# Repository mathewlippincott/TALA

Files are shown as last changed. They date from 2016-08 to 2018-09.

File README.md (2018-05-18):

### Introduction to the TALA
The TALA, or Tethered Aerodynamic Lifting Anemometer, is a type of [Kite Wind Speed Meter](https://github.com/mathewlippincott/Kite-Wind-Speed-Meter) or anemometer, a device for measuring the wind speed at the kite using ground-based measurements. 
The TALA repository consists of the [TALA kite](TALA_Kite), kite-specific [corrections to ground-based measurements](TALA_Measurement), as well as a kit of recommended tools for taking the required ground based measurements. Together these components form the TALA kit.
 
### Current TALA kit 
* The [TALA kite](TALA_Kite)
* [Lookup tables and equations](TALA_Measurement) for extrapolating air speed from measurments by:
 * correcting altitude measurements for line sag
 * correcting wind speed measurements for air density
* A [Measurement procedure](TALA_Measurement)
* Measurement equipment:
 * Spring scale for line tension
 * marked kite line for counting the amount of line in the air (or fishing line length counter) 
 * compass for wind direction
 * inclinometer for the angle of the kite 
 * thermometer for ground temperature
 * barometer for ground pressure

### Designers of the TALA
The kite was originally designed by Raymond P. Holland Jr. and adapted by Charles F. Woodhouse for anemometry into the TALA product sold by Approach Fish until some time in the early 1990's. The invention is covered by expired US patents 3,767,145, 4,058,010, 4,152,933 & 4,221,351.
	These plans are released under the [CERN OHL 1.2](LICENSE.MD), compiling [ongoing Public Lab research](www.publiclab.org/wiki/kite-anemometers) on the TALA into a DIY kit.
	
The TALA was imagined as an automated kite flight and measurement system providing local weather conditions at airports, but was usually flown by hand with a spring gauge used in the current TALA kit. Learn more about the [TALA and kite anemometer research in the Public Lab Wiki.](https://publiclab.org/wiki/kite-anemometers)

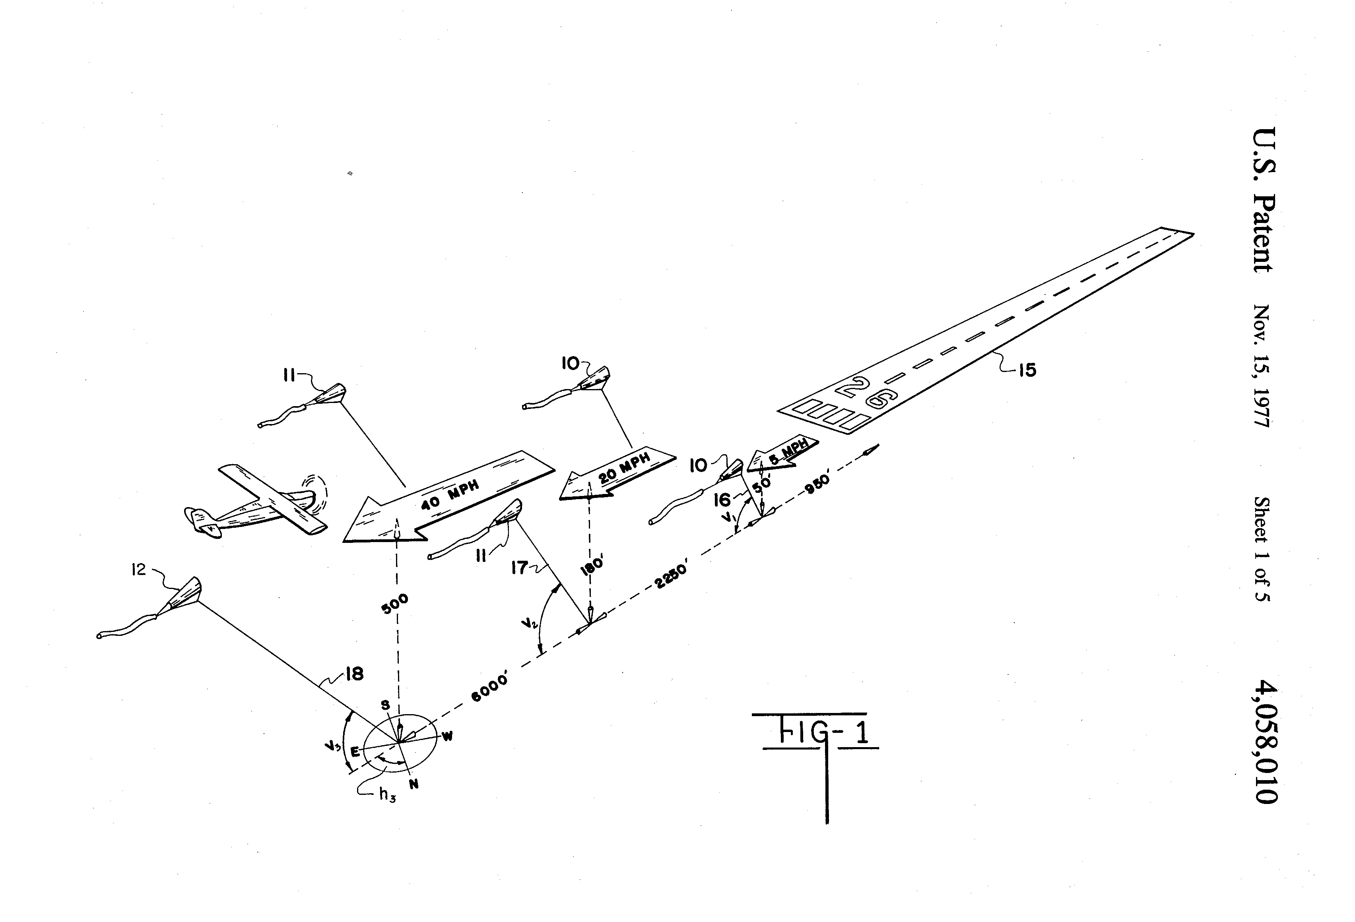
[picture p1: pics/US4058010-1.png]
TALAs at an airport


### About this project
The TALA repository is a project of [Mathew Lippincott](headfullofair.com) and [@Ecta64](http://publiclab.org/profile/ecta64) to create a stable device replicating the TALA and licensed under [CERN OHL 1.2](LiCENSE.md).

To read more about using kite anemometers and find resources and sources used in this repository, visit [headfullofair.com/tags/kite-anemometers](headfullofair.com/tags/kite-anemometers). 

### [contributing](contributing.md)
To learn more about contibuting, please read our [contribution guidelines](contributing.md).

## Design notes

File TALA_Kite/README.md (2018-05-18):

### The TALA Kite
The TALA kite is a type of sled kite. It is 1500cm^2 of surface area and the main sheet weighs 16g.  With all the rigging it weighs 18g.

All dimensions are in the TALA kite CAD file [TALA.dxf](TALA.dxf).  This 2D CAD file was created with the open source program [QCAD](http://qcad.org).

The instructions for maintenance and rigging are re-written from advice in the TALA manual. To make a TALA kite see [TALA Assembly](TALA_Assembly.md).

#### TALA Kite rigging adjustment
Tow the TALA without a tail attached behind an automobile in dead air.  IF the TALA veers to the left, add one or two half hitches to the left side of the kite’s bridle (as you view it in flight).  Continue towing adjustment unti the TALA is stable at 10m/s 

Now attach a tail and tow at 15m/s.  If the TALA veers to the right, shorten the left tail bridle with one or two half hitches.  Once stability is achieved, increase speed to 25m/s and repeat. 

_(ADD CONVERSIONS to MPH/KPH)_

#### Kite Maintenance
The Kevlar line used for the TALA does not stretch and makes poor knots.  Because of this, it is recommended that the snap swivel on the kevlar line be reattached periodically with a new crimped fastener. 

#### Kite Storage
Lay bridle on the center panel, fold side panels to the center.  Roll sides tightly to meet the center and insert tail-end first into a packing tube 1” (2.5cm) in diameter.

[picture]

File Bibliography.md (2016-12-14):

Most of the following papers treat the kite in a simplified manner, as a flat plane inclined into the wind.  Those dynamics are explained in more depth in the book:

Komura, Hirotsugu & Ito, Toshio. "Kites: The Science and the Wonder" Japanese Publications Inc. Tokyo: 1983. ["Tako No Kagaku" Shogakukan Publishing. Tokyo: 1979]

__General Tethered Anemometry:__

Chow, W.Y, & R.H. Kirchhoff. “Tethersonde and Kite Anemometer Evaluation.” PNL-6708, Pacific Northwest Laboratory. Subcontractor Report for US DOE. Richland: October 1988.
[Link](http://www.osti.gov/scitech/biblio/6884455/)

Hobbs, Stephen E. “A Quantitative Study of Kite Performance in Natural Wind with Application to Kite Anemometry.” PhD Thesis, Ecological Physics Research Group, Cranfield Institute of Technology. Cranfield: April 1986. 
[Link](https://dspace.lib.cranfield.ac.uk/bitstream/1826/918/2/sehphd2a.pdf)

__TALA Anemometry:__

Woodhouse, Charles F. “Tethered Aerodynamically Lifting Anemometer (TALA).” The Boulder Low-level Intercomparison Experiment, NOAA/ERL Wave Propagation Laboratory, National Center for Atmospheric Research (NCAR).  Boulder: June 1980.
[Link](https://archive.org/details/boulderlowleveli00kaim)

Kunkel, Kenneth E. “Evaluation of a Tethered Kite Anemometer.” ASL-TR-0076, US Army Atmostpheric Sciences Laboratory.  White Sands: February 1981.

Kullgren, Thomas E. Finley, Thomas C. Boyce, Steven C.  “Academy Wind Site Survey: Methodologies for use by the Air Force. Final Report, May 1977-December 1980.” AD-A129 581, Department of Engineering Mechanics and Department of Civil Engineering, United States Air Force Academy. Tyndall Air Force Base: 1983. 
[Link](https://publiclab.org/system/images/photos/000/010/724/original/TALA_USAF_site.pdf)

Daniels, Anders. “Turbulence Assessment at Potential Turbine Sites.” Windpower ’96 - Proceedings of the American Wind Energy Association, p 369-378. Denver: June 1996.
[Link](http://www.osti.gov/scitech/biblio/447473-turbulence-assessment-potential-turbine-sites)

__TALA in Education__

Bertrand, M and Donnelly, J. D. Go Fly a Kite! the Science Teacher pp 39-41 Volume 53: March 1986

__Studies conducted with the TALA:__

Taylor P.A. & H.W. Teunissen.  “Askervein ’82: Report on the September/October 1982 Eperiment to Study Boundary-Layer Flow over Akervein, South Uist.” MSRB-83-8, Meteorological Services Research Branch, Amospheric Environment Service. Downsview: November 1983.

Taylor, P.A. & H.W. Teunissen.  “The Askervein Hill Project: Report on the September/October 1983 Main Field Experiment.” MSRB-84-6, Meteorological Services Research Branch, Amospheric Environment Service. Downsview: December 1985.

Snyder W.H, Lawson R.E., Thompson R.S, & Holzworth G.C. “Observations of Flow Around Cinder Cone Butte, Idaho.” EPA-GCC17-SC-150, US Environmental Protection Agency. Research Triangle Park: June 1980.
[Link](http://nepis.epa.gov/Exe/ZyPURL.cgi?Dockey=2000XGYQ.txt)

Neal, D. “Wind Flow and Structure over Gebbies Pass, New Zealand.” Thesis, University of Canterbury New Zealand. Canterbury: December 1979.
[Link](http://ir.canterbury.ac.nz/handle/10092/7568)

Baker, Robert W. & Hewson, E. Wendell. “Network Wind Power Over the Pacific Northwest, Progress Report October 1979-September 1980.” DOE/BP-58. Bonneville Power Administration. Portland: October 1980. 
[Link](http://www.osti.gov/scitech/biblio/6373484)

Zambrano, T.G. “Assessing the Local Windfield with Instrumentation.” PNL-3622, Pacific Northwest Laboratory. Richland: October 1980.
[Link](http://www.osti.gov/scitech/biblio/6465288/)

-----------
__Further documents unretrieved:__

__Aerodynamics:__

Huang, K.H. ; Shieh, C.F. ; Frost, W. “Analysis of a kite anemometer: final report. REPORT # DOE/ET/20242-81/2” DE82009058 . FWG Associates, Inc., Tullahoma, TN (USA): December 1981.
[Link](http://www.osti.gov/scitech/biblio/5417476)

Kirchhoff, R. H., F. C. Kaminsky, and S. D. Pelmulder. "Measurement of atmospheric turbulence using kites." Ninth ASME Wind Energy Symposium- Presented at the Thirteenth Annual Energy-Sources Technology Conference and Exhibition, New Orleans, LA, USA, 01/14-18/90. 1990.

__Field Use:__

A low level wind measurement technique for wind turbine generator siting. Baker, R. W.; Whitney, R. L.; Hewson, E. W. Wind Engineering, vol. 3, no. 2, 1979, p. 107-114.

The Kettles Hill Project: Field observations, wind-tunnel simulations and numerical model predictions for flow over a low hill. Boundary-Layer Meteorology, 1988, Volume 43, Number 4, Page 309, J. R. Salmon, H. W. Teunissen, R. E. Mickle, Show All (4)

The influence of model scale on a wind-tunnel simulation of complex terrain. D. Neal, Vickers Dawson, Crayford, Kent, Gt. Britain. Journal of Wind Engineering and Industrial Aerodynamics Volume 12, Issue 2, July 1983, Pages 125-143

Full-scale measurements of the wind regime over a saddle, and correlation with wind-tunnel tests. D. Neal Boundary-Layer Meteorology March 1982, Volume 22, Issue 3, pp 351-371

Note: A thermally stable tension meter for atmospheric soundings using kites
K. T. Walesby1,a) and R. G. Harrison1,b). Rev. Sci. Instrum. 81, 076104 (2010)

Sherry, B. J. "The Use of a Flagpole in Calibrating Kite Anemometers and also for Observing at Close Range the Behavior of Kites in the Air." Monthly Weather Review 44 (1916): 327.

The Askervein hill project: A finite control volume prediction of three-dimensional flows over the hill. G. D. Raithby, G. D. Stubley, P. A. Taylor. Boundary-Layer Meteorology
May 1987, Volume 39, Issue 3, pp 247-267

Wake measurements behind a large horizontal axis wind turbine generator. Robert W. Baker, Stel N. Walker. Solar Energy Volume 33, Issue 1, 1984, Pages 5-12
	
Case study of wind turbine generator siting in complex terrain. Vachon, W.A. ; Downey, W.T. ; Madio, F.R.Proc. Annu. Meet. - Am. Sect. Int. Sol. Energy Soc.; (United States); Journal Volume: 3.2; Conference: American section of the International Solar Energy Society conference, Phoenix, AZ, USA, 2 Jun 1980

EAGAN, RC, L. E. ANNEN-Dames, and Park Ridge Moore. "DATA ACQUISITION AND ANALYSIS FOR WIND TURBINE SITING IN THE UPPER MID WEST." Second ASME Wind Energy Symposium: presented at 6th Annual Energy-Sources Technology Conference and Exhibition, Houston, Texas, January 30-February 3, 1983. American Society of Mechanical Engineers, 1983.

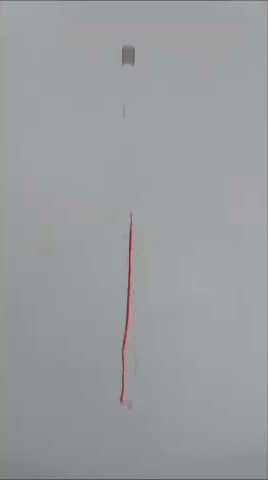
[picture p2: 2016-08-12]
pics/tala.gif

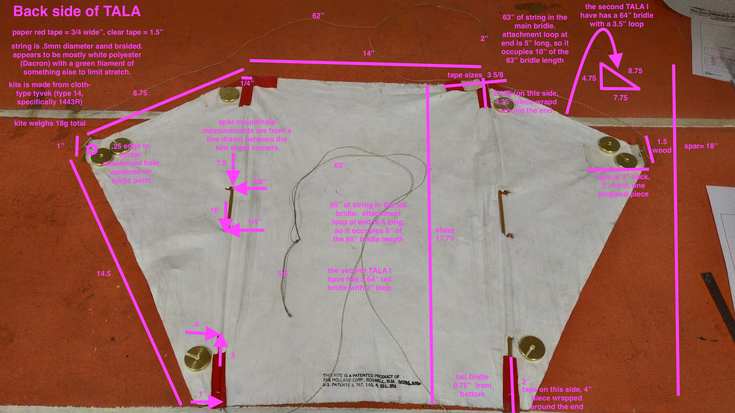
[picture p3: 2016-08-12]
pics/TALAannotated.jpg

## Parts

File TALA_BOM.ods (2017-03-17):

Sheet: kite materials
Required Material | Function | quantity | interchangeable? | current material | supplier | quantity sold | price | website | alt | notes
Essentials:
main sheet tyvek | main kite fabric | 3.75 sq ft (18” x 30”) | no | Tyvek type 1443R | Into the Wind | 1-20 yards | 3.5 | http://intothewind.com/Item--i-402 |  | cutoffs are sold all over the place for cheap
birch spars | spars and bridle attachment | 39” | for same product | 1/8” birch dowels (mcmaster 9683K51) | mcmaster carr | 50 x 48” | 13.73 | https://www.mcmaster.com/#9683k51/=16s8v0f
3/4” Artists tape | spar adhesive | 24” | for same product | Dick Blick 24143-3014 | Dick Blick | 60 yards | 7.19 | http://www.dickblick.com/items/24143-3014/ | https://www.enasco.com/product/9730189(A) | nasco 'colored masking tape' may be the same thing
1.5” x .002” transparent packing tape | bridle adhesive | 10” | for same product | PP packing tape 002” thick with an acrylic adhesive. 3M #375 | mcmaster carr | 55 yards | 8.69 | https://www.mcmaster.com/#76865a21/=16s8zrh
20lb test braided dacron fishing line.483mm dia | kite rigging | 200” | for same material | TufLine.483mm braided dacron #20 test | tackle direct | 100 yards | 5.99 | http://www.tackledirect.com/tuf-line-20-lb-braided-dacron-100-yards.html
15kg test kevlar line .25mm diameter | kite flying line marked every 10' | 500' | for same material | Size 69 (tex 60) thread kevlar thread |  | 209-6700 yards | 15 | http://www.thethreadexchange.com/miva/merchant.mvc?Screen=CTGY&Category_Code=kevlar_thread_Size_069
20lb test #10 brass duolock snap swivels | connecting tail and flying line | 2 | for same mass | VMC duolock snap swivel #10 | tackle direct | 5 | 2.49 | http://www.tackledirect.com/vmc-duolock-snap-swivels.html

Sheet: kite making tools
Required Material | Function | quantity | interchangeable? | current material | supplier | quantity sold | price | website | alt | notes
Essential:
1/4” hole punch | making hole for bridle | 1 per class | for same size |  | mcmaster carr | 1 | 3.6 | https://www.mcmaster.com/#12885t21/=16srowe
craft knife | cutting main sheet | 1 per kit | or sharp scissors | X-acto | mcmaster carr | 1 | 3.14 | https://www.mcmaster.com/#35435a11/=16srpbg
Very Helpful:
thumb tack | transferring pattern from paper to the main sheet | 1 per kit |  | thumb tack | mcmaster carr | 100 | 4.73 | https://www.mcmaster.com/#57115t22/=16sazf4
cardboard | Making a master kite pattern, protecting surfaces | 4 sq ft per kit |  | dumpstered cardboard | the garbage | omg you paid for cardboard I'm dying
fine point permanent marker | transferring print pattern to tyvek | 1 per kit | yes | sharpie fine/u;trafine dual tip point | mcmaster carr | 1 | 2.39 | https://www.mcmaster.com/#1661t38/=16sb0it
printer | printing kite pattern | 6x 8.5” x 11” paper | color or b&w

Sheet: measurement & flight
Required Material | Function | quantity | interchangeable? | current material | supplier | quantity sold | price | website | alt | notes
Bare Bones:
calibration weight | calibrate spring scale in the field |  |  | 250g slotted weight set | Nasco | 1 | 22 | https://www.enasco.com/product/SB26385M
High-tension spring scale | tesnsion measurement | 1 | yes | nasco spring scale, 2000g | nasco | 1 | 4.2 | https://www.enasco.com/product/SB25290M
Low-tension spring scale | tension measurement | 1 | yes | nasco spring scale, 500g | nasco | 1 | 4.3 | https://www.enasco.com/c/science/Measurement/Spring%20Scales/Economy%20Spring%20Scales/
carabiner | attaching spring scale to kite line | 1 | yes | lightweight aluminum, keychain-style. | Into the Wind | 1 | 2 | http://intothewind.com/Item--i-6551 | https://www.windycitynovelties.com/carabiner-key-chains.html | windy city novelties is 12/4.50
inclinometer | measuring kite angle | 1 | yes | protractor with a string and a weight | Nasco | 1 | 0.25 | https://www.enasco.com/product/TB02088T
compass | measuring kite direction | 1 | yes | compass |  | 1 | 2.95 | https://www.enasco.com/product/SB51128M
thermometer | temperature | 1 | yes | thermometer | nasco |  | 2.05 | https://www.enasco.com/product/TB17432T
pressure measurement | barometry | 1 | yes | estimation based on sea level and temperature
gloves | protecting hands from kite line | 1 pair | yes | leather palm work gloves | mcmaster carr | 1 | 2
line winder | winding line | 1 | yes, consider a bigger reel for easier handling (9” or larger) or a fishing reel | 5” hoop winder | Into the Wind | 1 | 7 | http://intothewind.com/Item--i-1250
lmarked line | altitude measurement | 1 | yes (see line counters & line counting fishing reels) | use a permanent marker to mark flight line ever 10' | you
Helpful substitutes & additions
Inclinometer & compass | measuring kite angle & direction | 1 | yes | Brunton TruArc 7 | Brunton | 1 | 34 | http://www.brunton.com/products/truarc-7
Thermometer +/- 1 deg C | temperature | 1 | yes | analog thermometer | mcmaster carr | 1 | 6.51 | https://www.mcmaster.com/#11165k63/=16sa06h
line counter | count line as it leaves the ground | 1 | can be substituted for line marked every 10' or similar interval, clips to fishing rod. Can also be found integrated in a fishing reel | rapala lighted line counter | amazon. This is not a popular item anymore as it is usually a feature integrated into reels now. | 1 | 17 | https://www.amazon.com/Rapala-RLLC-Lighted-Line-Counter/dp/B001NXC7MM
line winder | winding line | 1 | yes, a fishing reel with integrated line counter | G-kitewooden winder | G-kites | 1 | 18 | https://www.gkites.com/store/
medium-tension spring scale | tesnsion measurement | 1 | yes | nasco spring scale, 1000g | nasco | 1 | 4.2 | https://www.enasco.com/product/SB25291M
Advanced & expensive:
Line counting Medium duty fishing reel 20# | line handling | 1 | yes, can substitute for any kite line-handling system. Some reels count line too | Okuma MA-30DXT Magda Pro line counter reel | tackle direct | 1 | 65 | http://www.tackledirect.com/okuma-ma-30dxt-magda-pro-line-counter-reel.html | http://www.cabelas.com/product/Penn-reg-LC-Cabelas-DepthMaster-reg-Trolling-Combo/751543.uts | cabelas sells the Penn 209LC which has a lower gear ratio (probably positive) and good ratings for 84, saving 5 bucks.
fishing rod 20# | line handling | 1 |  | shimano stimula | tackle direct | 1 | 25 | http://www.tackledirect.com/shimano-stimula-spinning-rods.html
barometer | pressure | 1 | yes, can substitute for estimation from sea level + temp | portable weather station or similar. Kestrel 5500, brunton ADC pro |  |  | 150 | http://www.trailspace.com/gear/brunton/adc-pro/

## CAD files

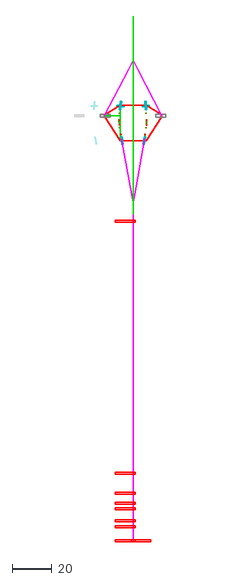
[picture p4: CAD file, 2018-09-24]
TALA_Kite/TALA.dxf
46.2 x 265.5

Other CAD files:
Kite_Plans/TALA.dxf

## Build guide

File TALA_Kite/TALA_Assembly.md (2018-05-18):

### Assembling the TALA

#### Materials:
* Kite main sheet and tail tassels are Tyvek type 1443R
* All wood is 1/8” birch dowel
* Spar tape is 3/4” Artists’ Tape 
 * (Dick Blick 24143-3014)
* Bridle attachment tape is 1.5” packing tape
 * NOTE: this size of tape is no longer manufactured. buy larger tape and cut it down to width.
* Kite rigging line is 50lb test braided dacron fishing line, .45mm in diameter
* Kite flying line is 15kg test kevlar line, .25mm diameter.   
 * This line is also known as trade size 69 (Tex 60) thread in the textile industry. It can be purchased through [Thread Exchange](http://www.thethreadexchange.com/).
* Snap swivels are 14 gauge brass.

#### Tools needed: 
* straight edge
* scissors or craft knife
* US standard 1/4” hole punch 

#### Assembly instructions
Print [1/2 sheet cut pattern](TALA-half-sheet-8.5x11.pdf) on 8.5x11” paper and assemble tiled sheets.

Tape as indicated.  Assembly diagram is for the back side of the kite. [print full-size tiled kite pattern](TALA-sheet-8.5x11.pdf)
_[ADD svg vector diagram]_

#### Step-by-step
_TBA_

#### Bridling
Both the attachment bridle and tail bridle are 60" pieces of string.  Both need a 2" attachment loop tied on with a larks head knot.

#### Tail assembly

##### How many tails? 
We have two original tails for the TALA which can be assumed to be described in the patent US421351.

The two tails may be two parts of a single tail, as described in the Air Force's vertical profiling procedure and elsewhere.  In this case the TALA would be flown with 1/2 tail in low winds and a full tail in high winds.

Alternatively, the two tails are two separate tails, one 1/2 length and the other full-length.

The TALA kite flies great with the shorter unweighted tail, and also flies great with the longer tail.

#### Materials and Design of the Tail 

Both tails are made from the same string as the bridle and have 1" x 10" Type 1441 Tyvek tassels tied into them. Both tails are clipped to the tail bridle by means of a 14 guage snap swivel.

The first tail is made with the same line that bridles the TALA kite, and can therefore be assumed to be original.

Total Length: 171.5"

Tassels are tied below the snap swivel at 9.5", 137", 147", 152", 155", 161", 164", and two tassels at 171".

The second tail is made from black line and does not appear to be original, although its use of a weight is described in the patent. It has a weight at the end.

* Total Length: 260.5"

* A 2.3g (35 grain) lead split-shot sinker is attached at 259.5"

* Tassels are tied below the swivel at: 78.5", 82", 84.5", 87.5", 98.5", 229", 235.5", 242", 244.5", 249", 252", 255.5", 260.5"-- two tassels on the end.

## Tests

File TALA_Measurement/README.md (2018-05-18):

### TALA measurements
Measurements should be taken manually according to the [United States Air Force Vertical Profiling Procedure.](USAF_TALA.md)

#### Determining velocity in relation to force on the kite
At ICAO standard Day Pressure of 1013.25mbar (sea level) at 15° C the TALA shows 2% accuracy to the equation:

V= 0.5144(N/0.01779)^0.510
Where V is m/s and N is Newtons

* When the lower half of the tail is disconnected, indicated air speed is lowered by 1% _(from the manual, page 8)_

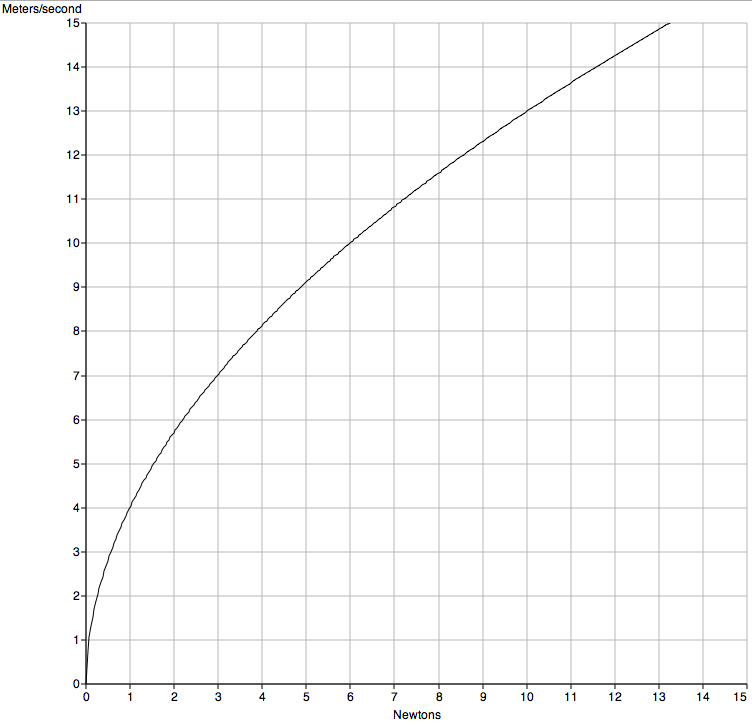
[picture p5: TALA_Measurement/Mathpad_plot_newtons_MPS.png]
V= 0.5144(N/0.01779)^0.510
 
_graph made with [mathpad](http://pubpages.unh.edu/~mwidholm/MathPad/)_

#### Correcting for temperature and pressure
Measurements need to be corrected for temperature or pressure, expressed in [“pressure altitude.”](http://www.srh.noaa.gov/images/epz/wxcalc/pressureAltitude.pdf) 

Pressure Altitude = (1-(P/1013.25)^0.190284)x145366

Where P is the measured pressure in millebar. By adding the altitude of the TALA to the pressure altitude measured at ground level, a pressure altitude correction can be obtained. The TALA manual suggests adding Indicated Air Speed (IAS) to  IASx%Correction to provide True Air Speed (TAS)

TAS=IAS + IASx%Correction

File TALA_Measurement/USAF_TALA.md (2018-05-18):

### USAF TALA vertical profiling procedure
For recording on [USAF TALA record sheet](TALA USAF_record_sheet.pdf)

1. Assemble reel and handle.
2. Calibrate measuring tube as described in owner’s manual.
3. Remove barometer and thermometer from carrying case and place in a sheltered location. Record temperature and pressure altitude.
4. Read fixed instrumentation if flying over such a site.
5. Launch kite to the first reel count directly over the selected site.
6. Record start time of the test.
7. Record inclination of the ridgecrest.
8. Record inclination to the kite and wind direction.
9. Record wind speed 10 times with each reading spaced by 15 seconds.
10. Repeat steps 8 and 9 one more time for a total of 20 wind speed readings.
11. Record inclination to the kite and wind direction.
12. Increase reel count for the next set of readings.
13. Return to step 7 and repeat steps 7-12 until the profile is complete.
14. Reel in the kite, again repeating steps 7-12 but now at decreasing reel counts.
15. Take final reading of fixed instrumentation if applicable.
16. Reduce data on a desktop computer or plot by hand.

*From Table 16, pages 52 and 53:*

Kullgren, Thomas E. Finley, Thomas C. Boyce, Steven C.  USAF (United States Air Force) Academy Wind Site Survey: Methodologies for use by the Air Force. Final Report, May 1977-December 1980. Department of Engineering Mechanics and Department of Civil Engineering, United States Airforce Academy, 1983. 

document AD-A129 581

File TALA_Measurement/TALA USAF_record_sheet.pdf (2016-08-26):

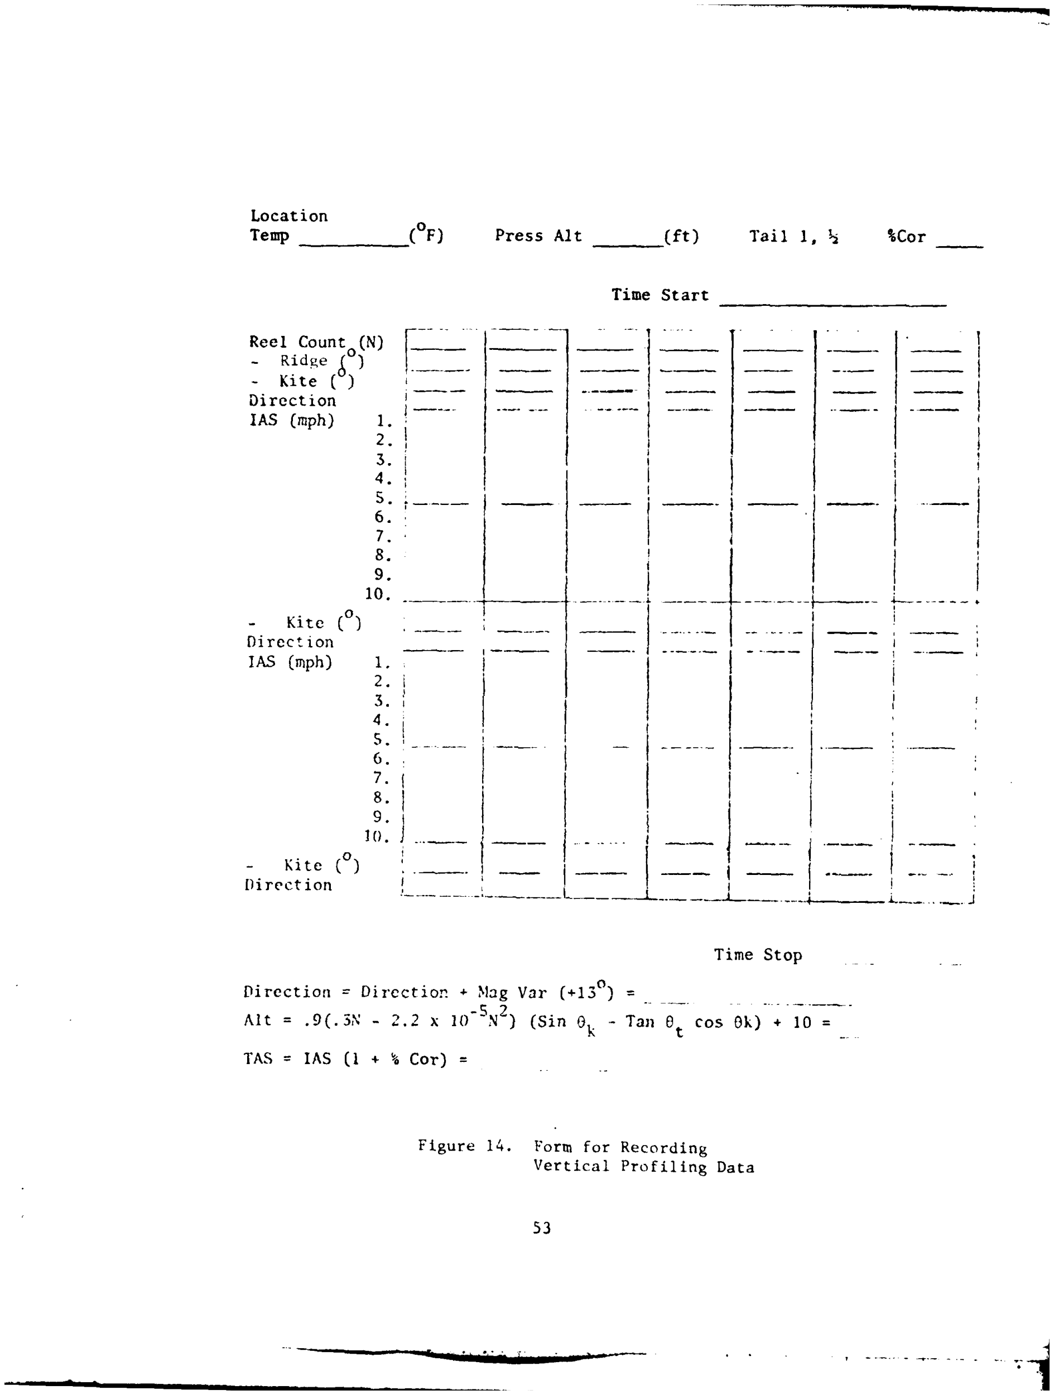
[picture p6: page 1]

Location
Temp | 0 F) | Press Alt | (ft) | Tail 1, | %Cor

Time Start

Reel Count (N) - Ridges) (0)

- Kite()
Direction
IAS (mph) 1.2.

4.

6.

10. ______ | _

7.

B.

9.
10.
Kite (o0
Direction

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
- Kite | ). | ... | ..
D]irection

Time Stop
Direction | =Direction | + Mag Vat (+13 ° | =
At=.9(.3,N - 21.2 x 10- 5N ² | (Sin 0 k | -Tan | e t | cos Ok) + 10=
TAS = IAS 01 + | Cot):
Figure 14. | Form for Recording Vertical Profiling Data

53

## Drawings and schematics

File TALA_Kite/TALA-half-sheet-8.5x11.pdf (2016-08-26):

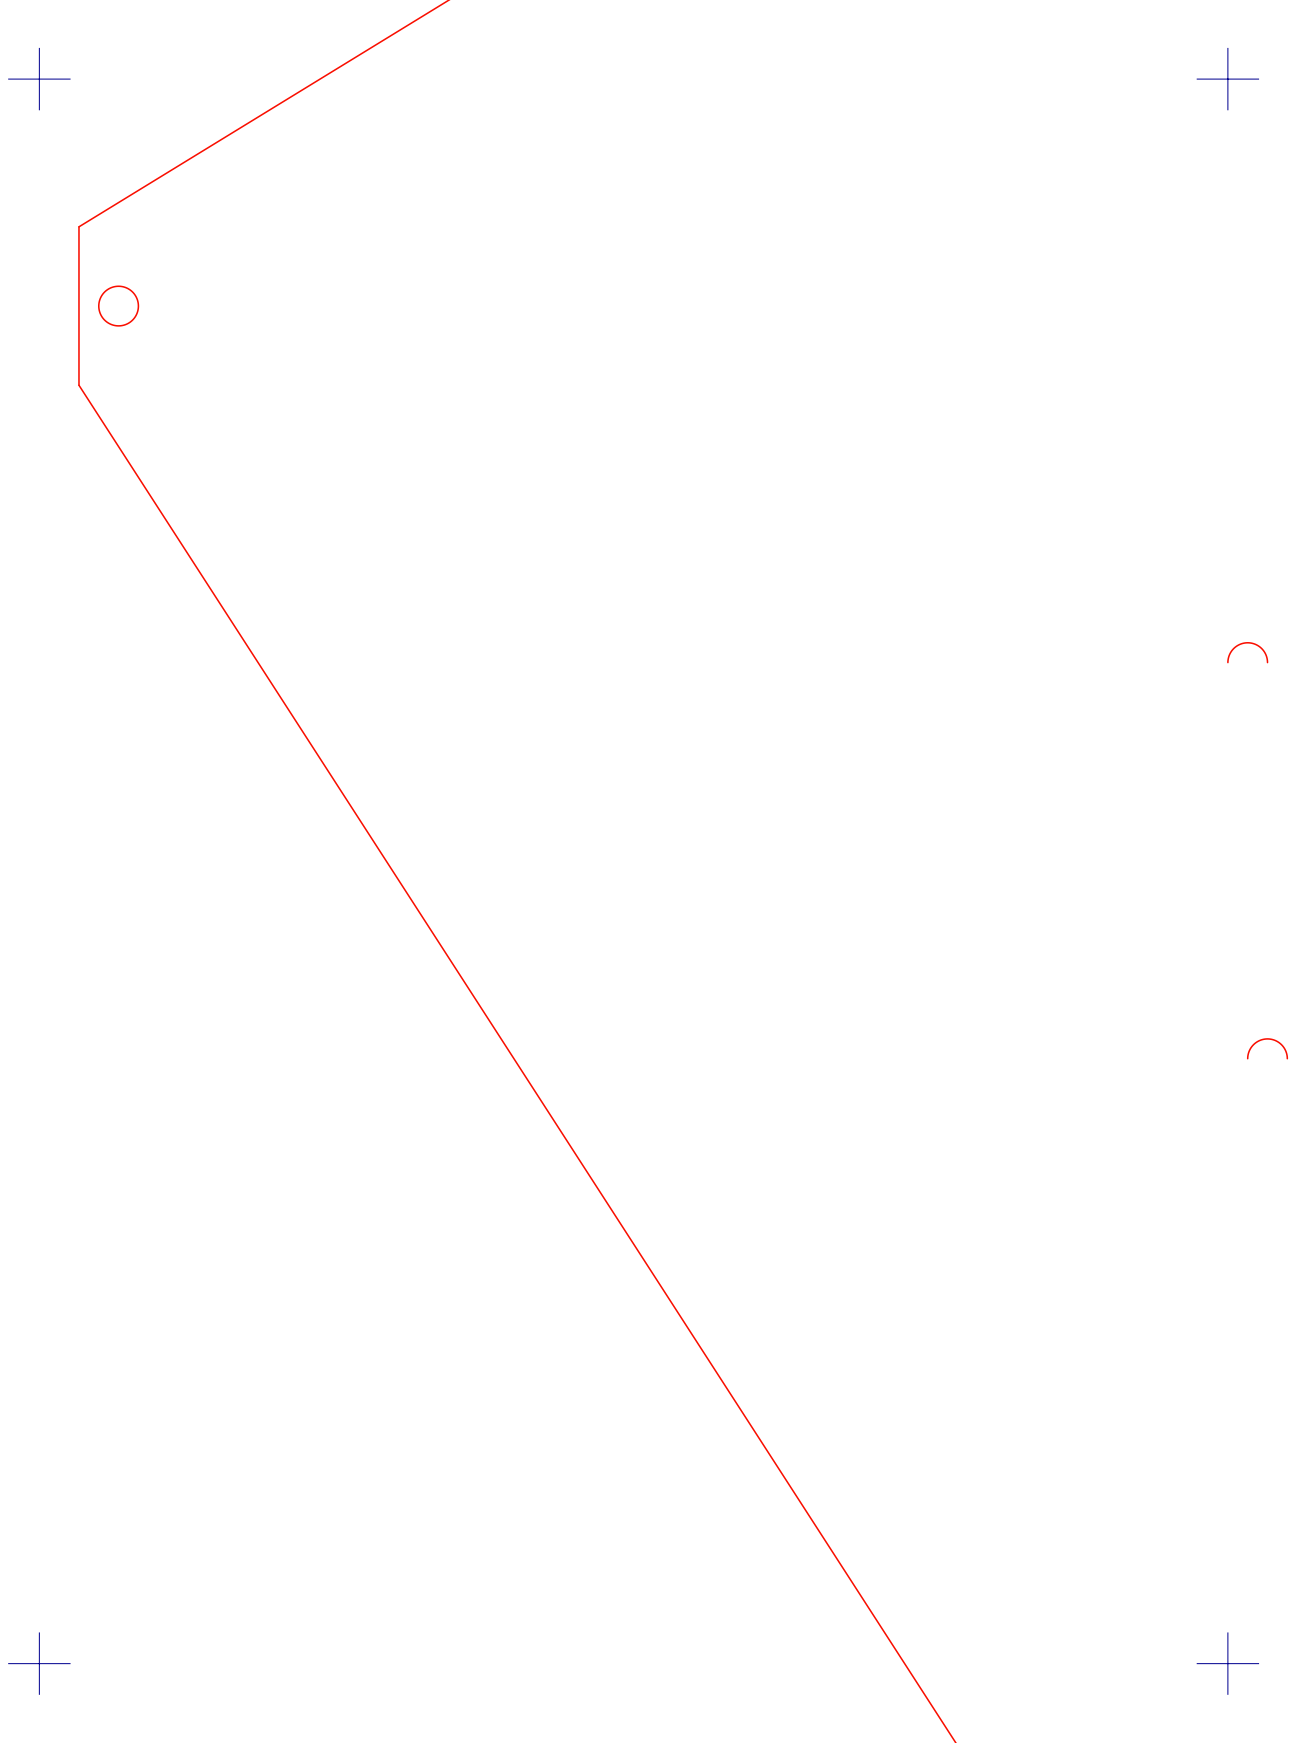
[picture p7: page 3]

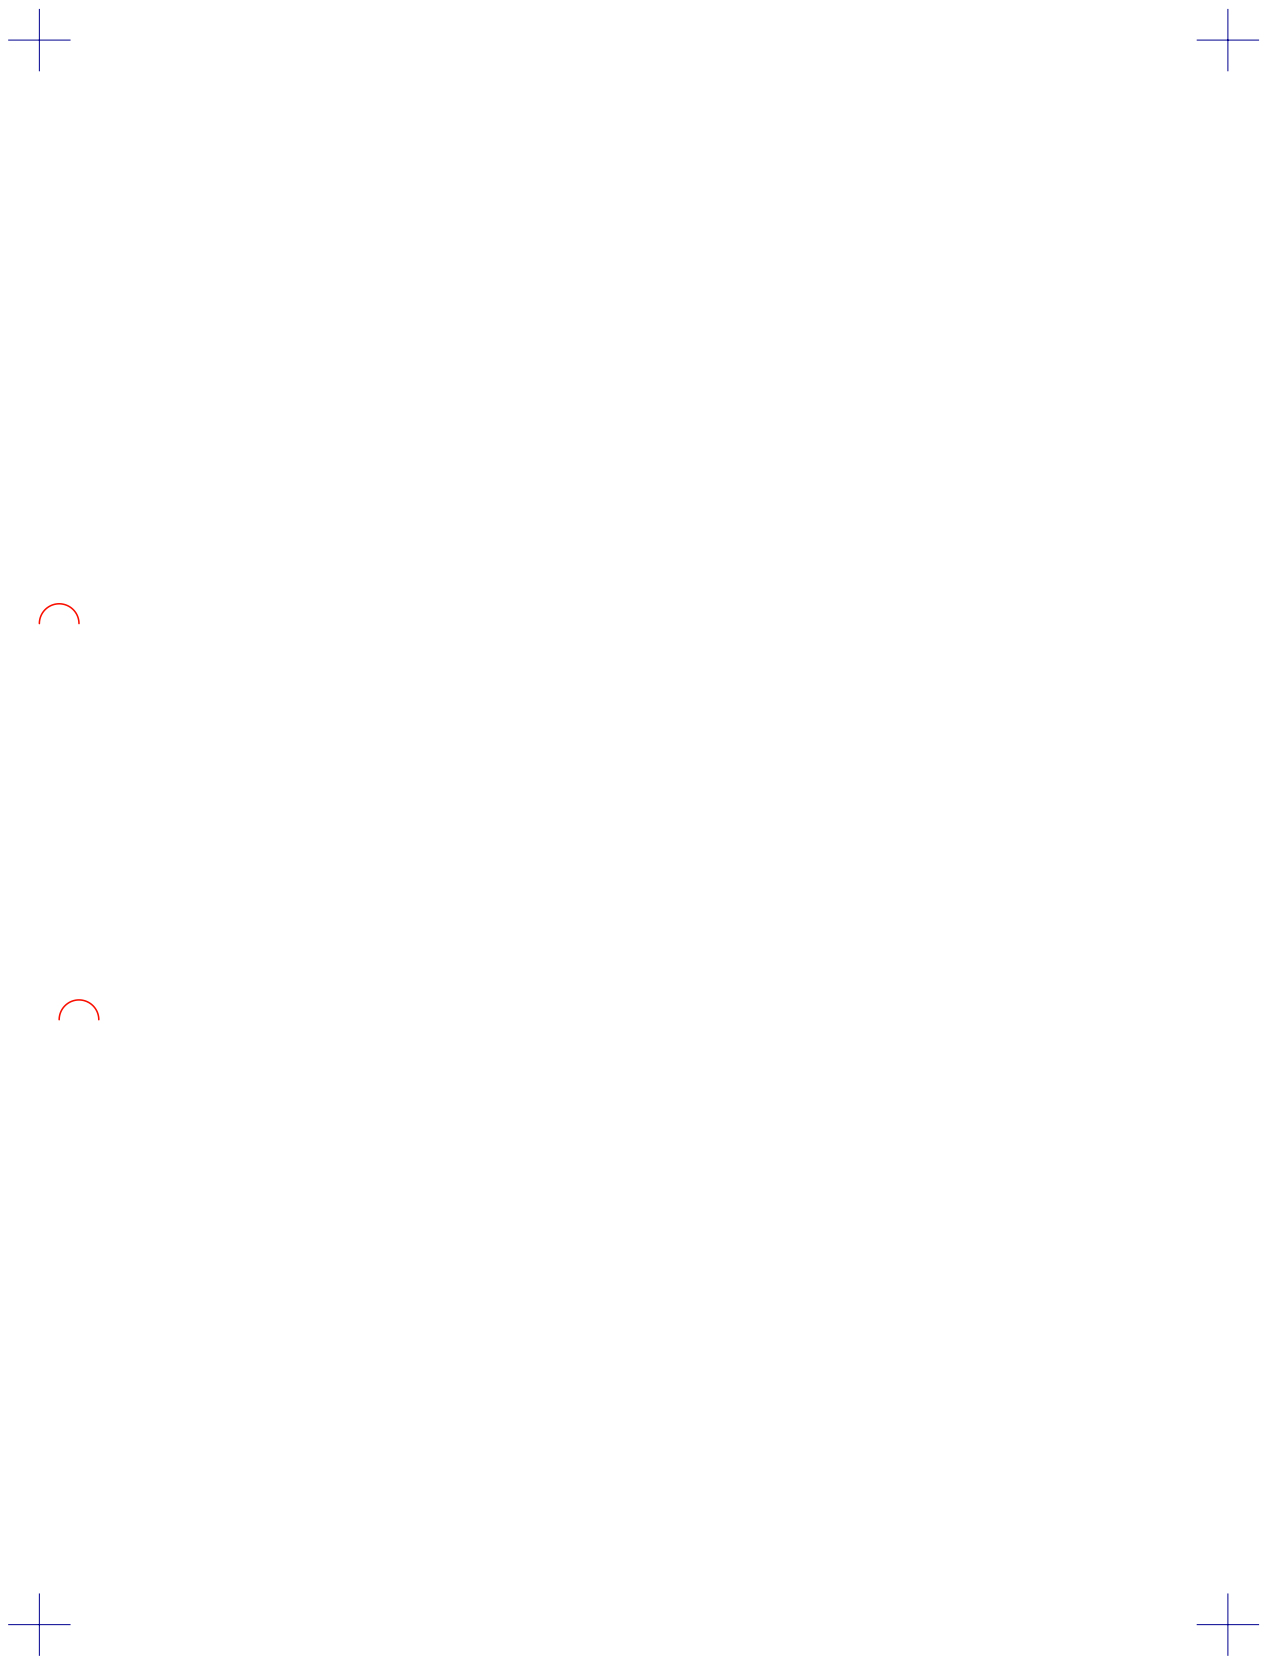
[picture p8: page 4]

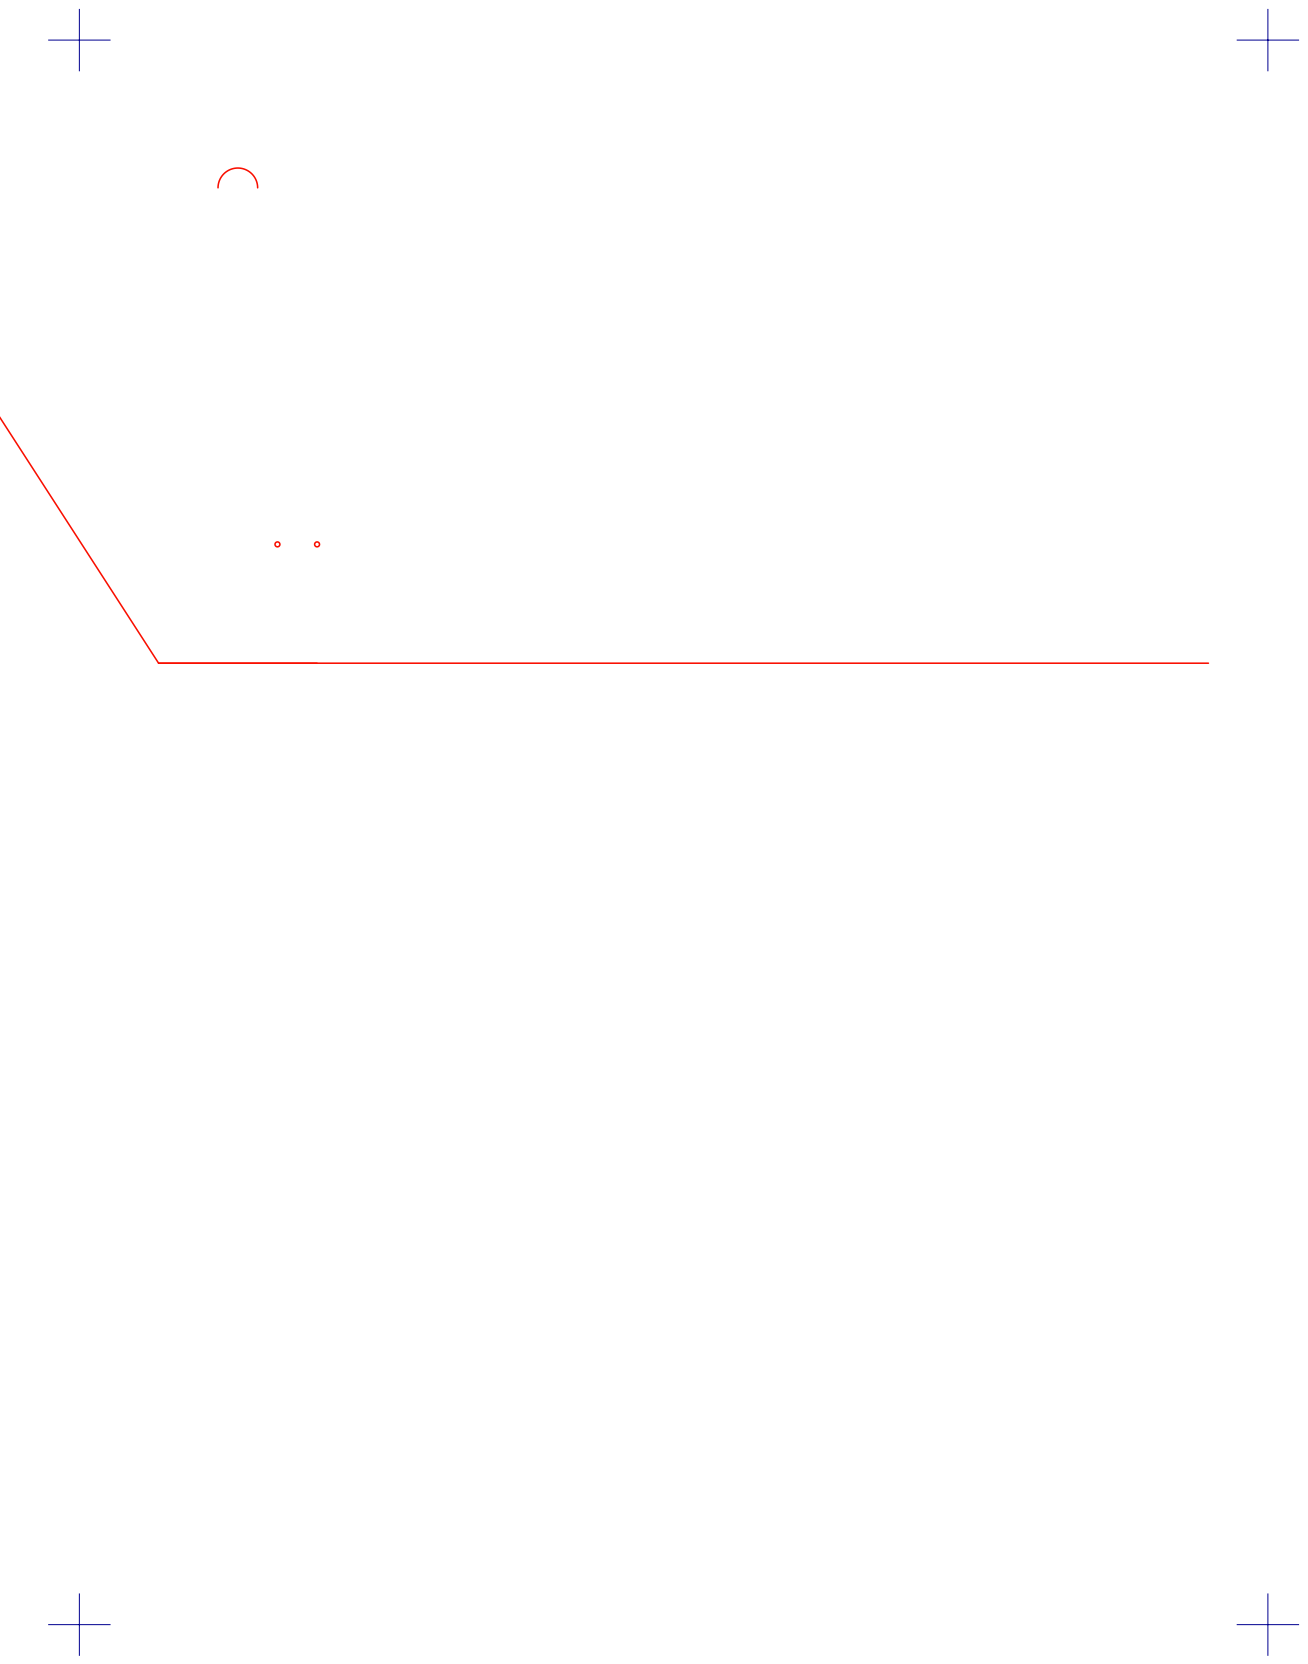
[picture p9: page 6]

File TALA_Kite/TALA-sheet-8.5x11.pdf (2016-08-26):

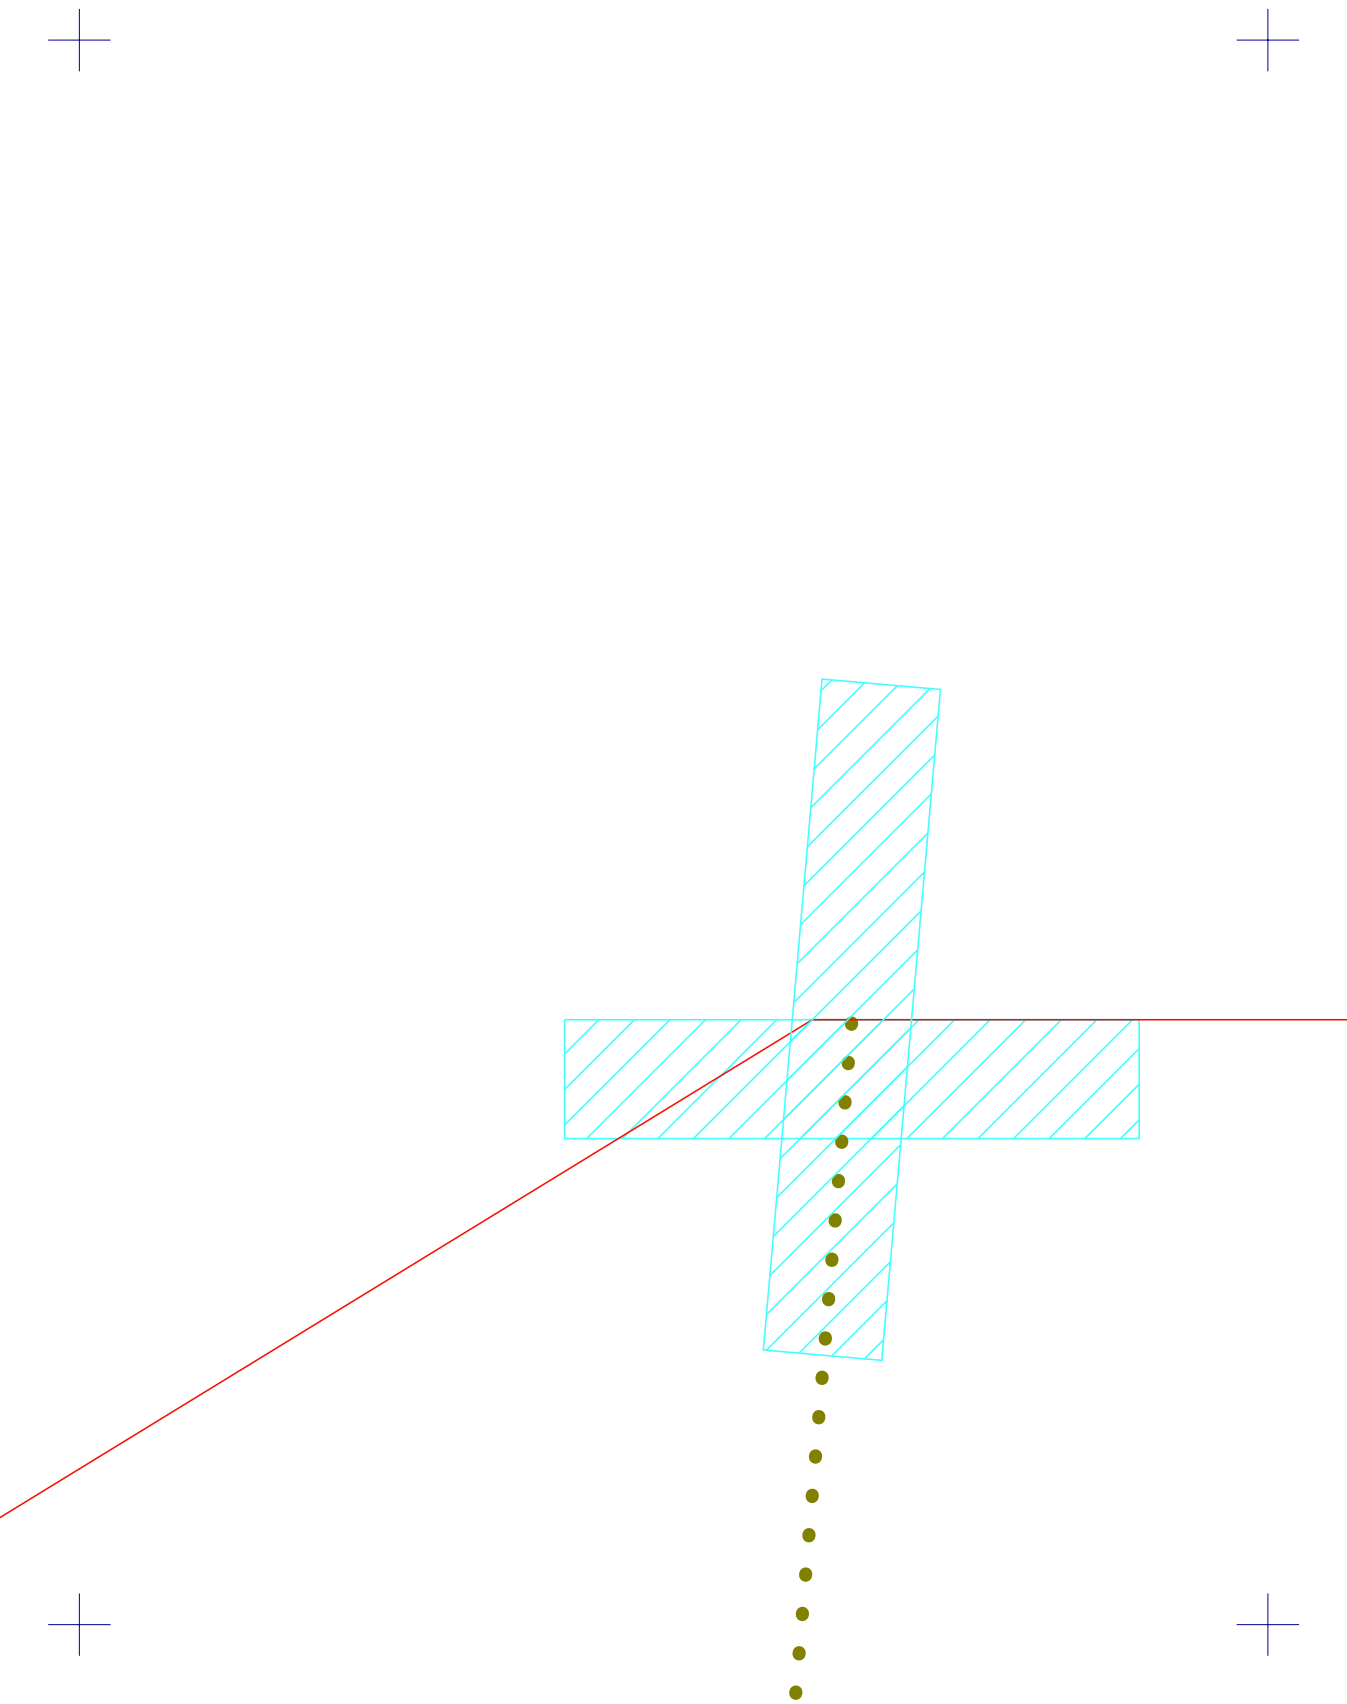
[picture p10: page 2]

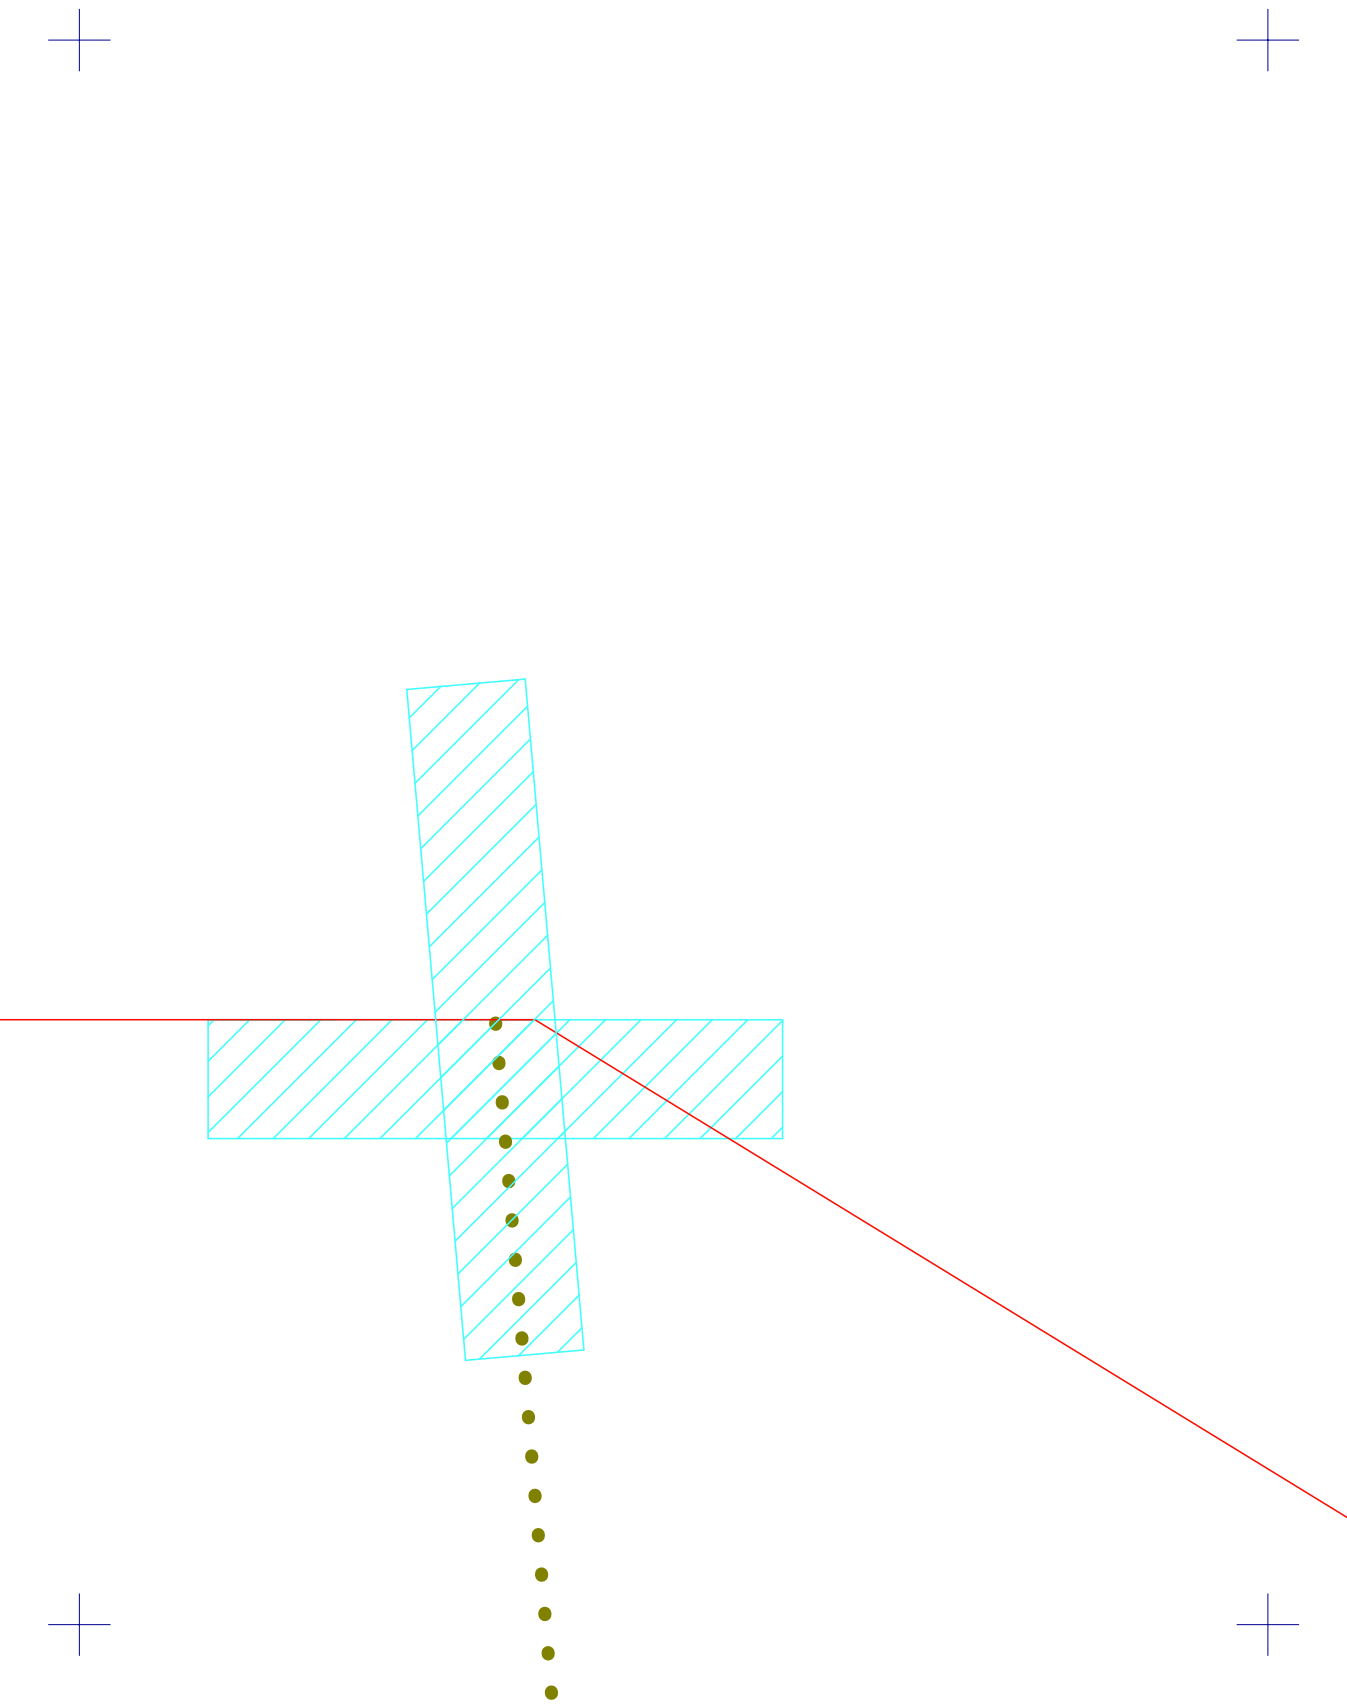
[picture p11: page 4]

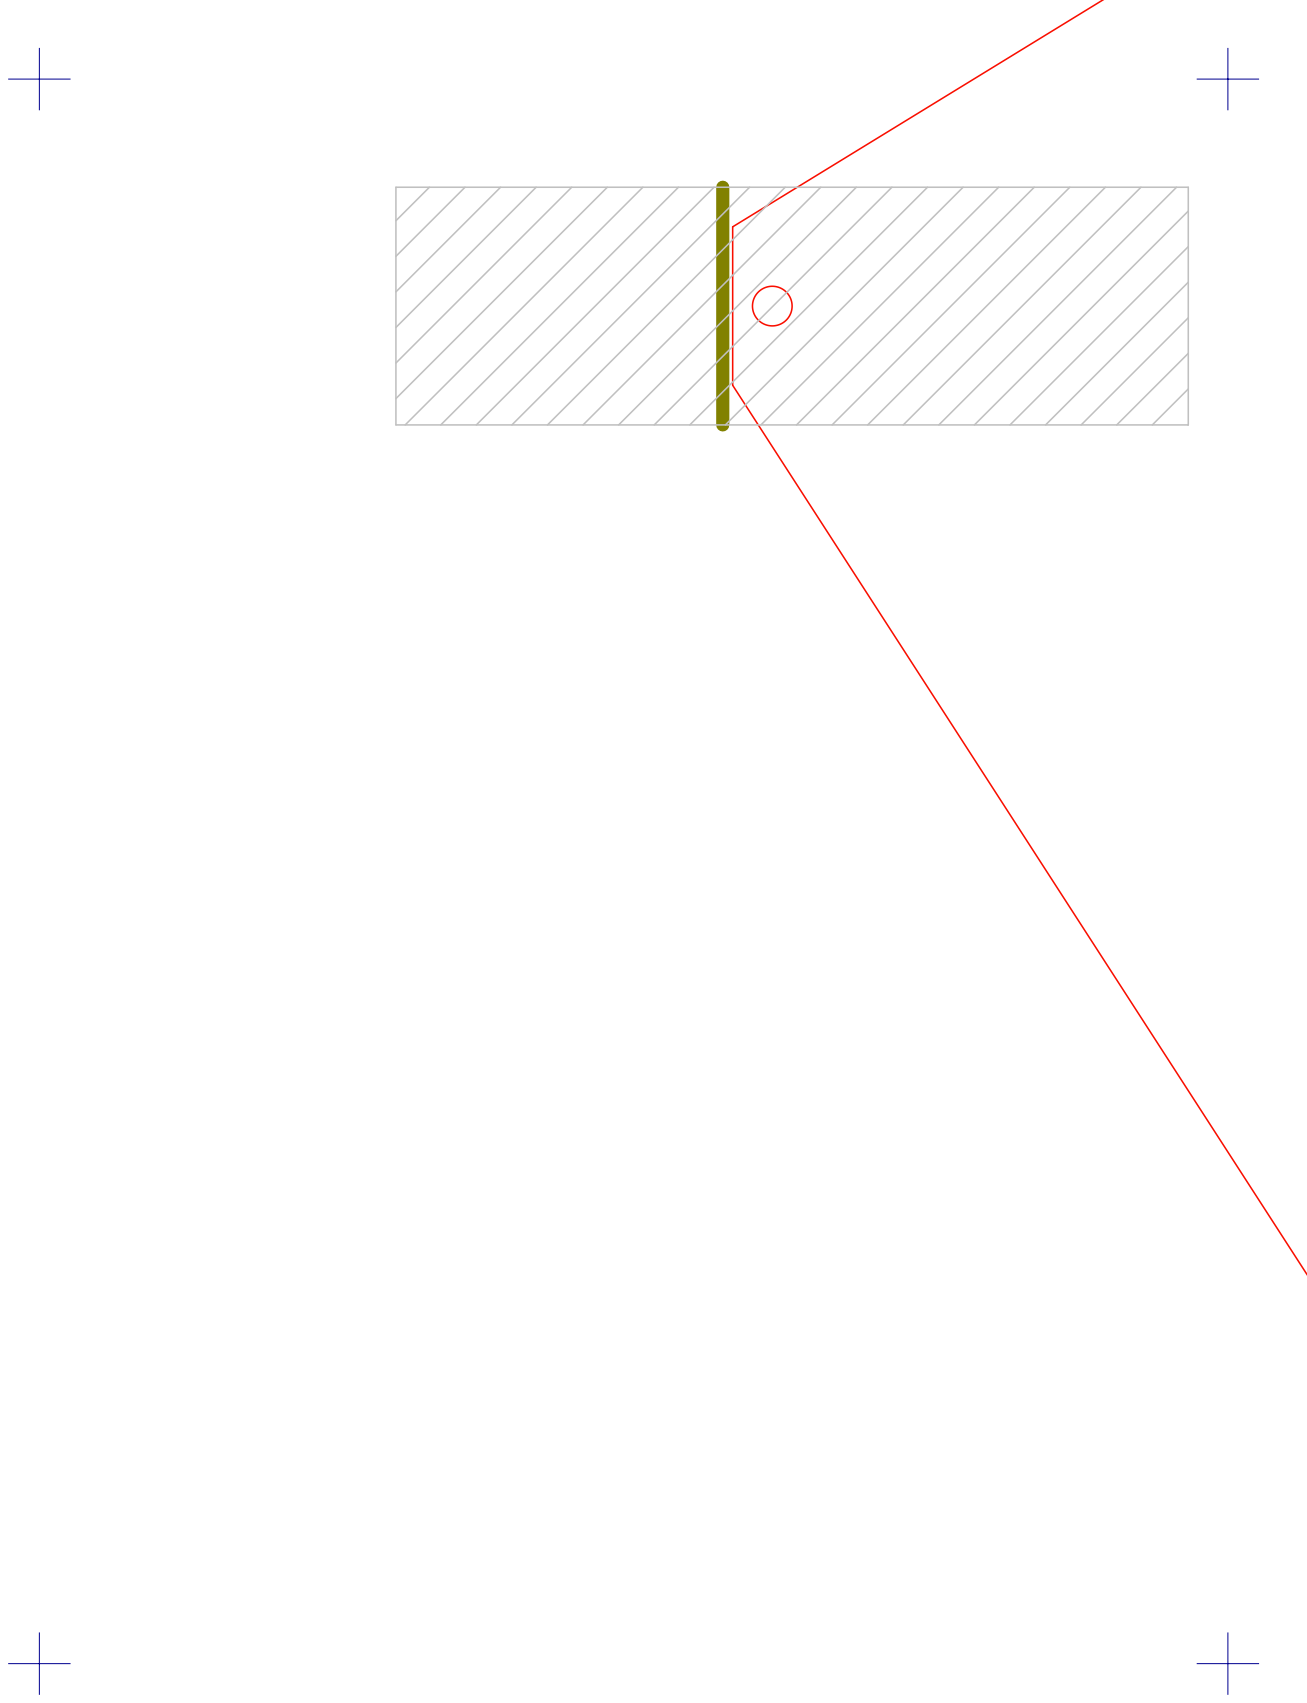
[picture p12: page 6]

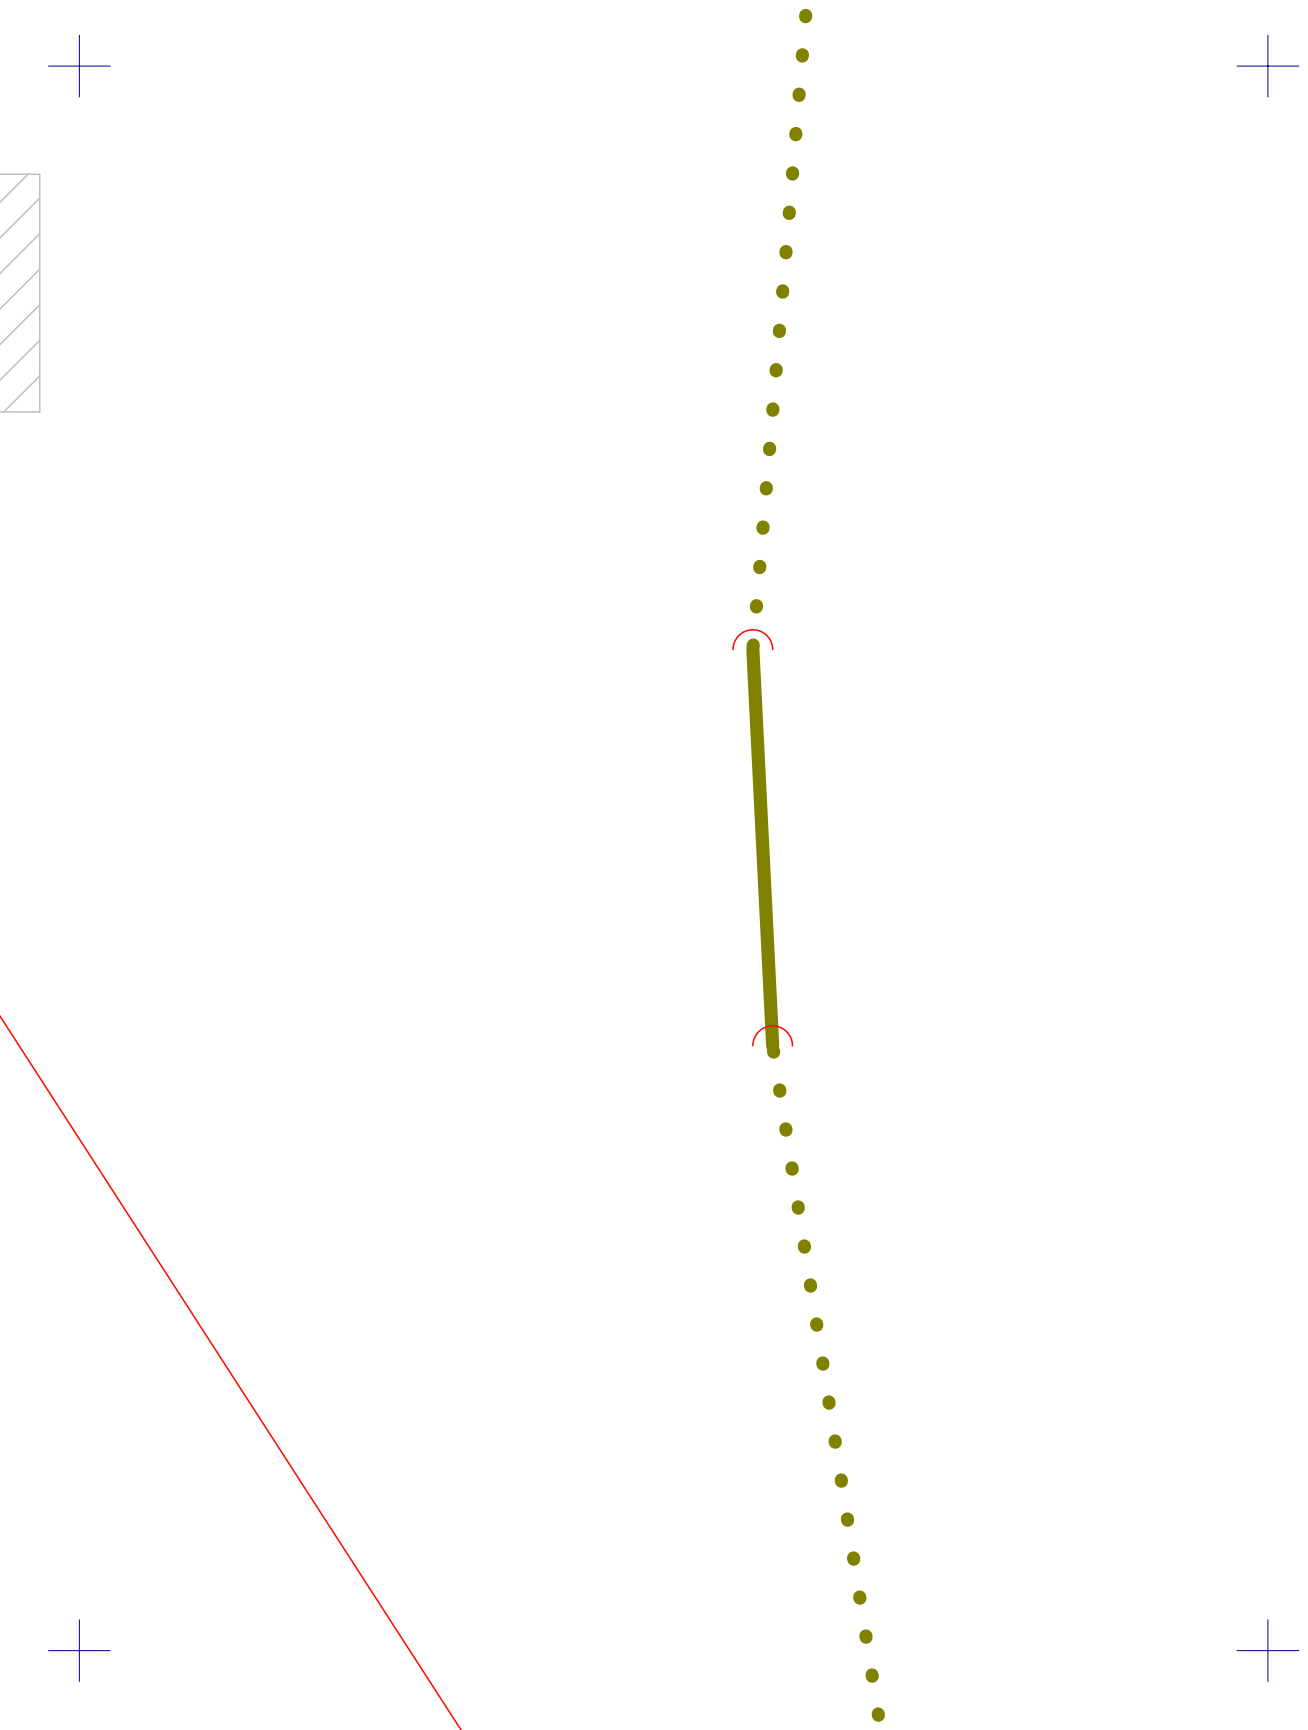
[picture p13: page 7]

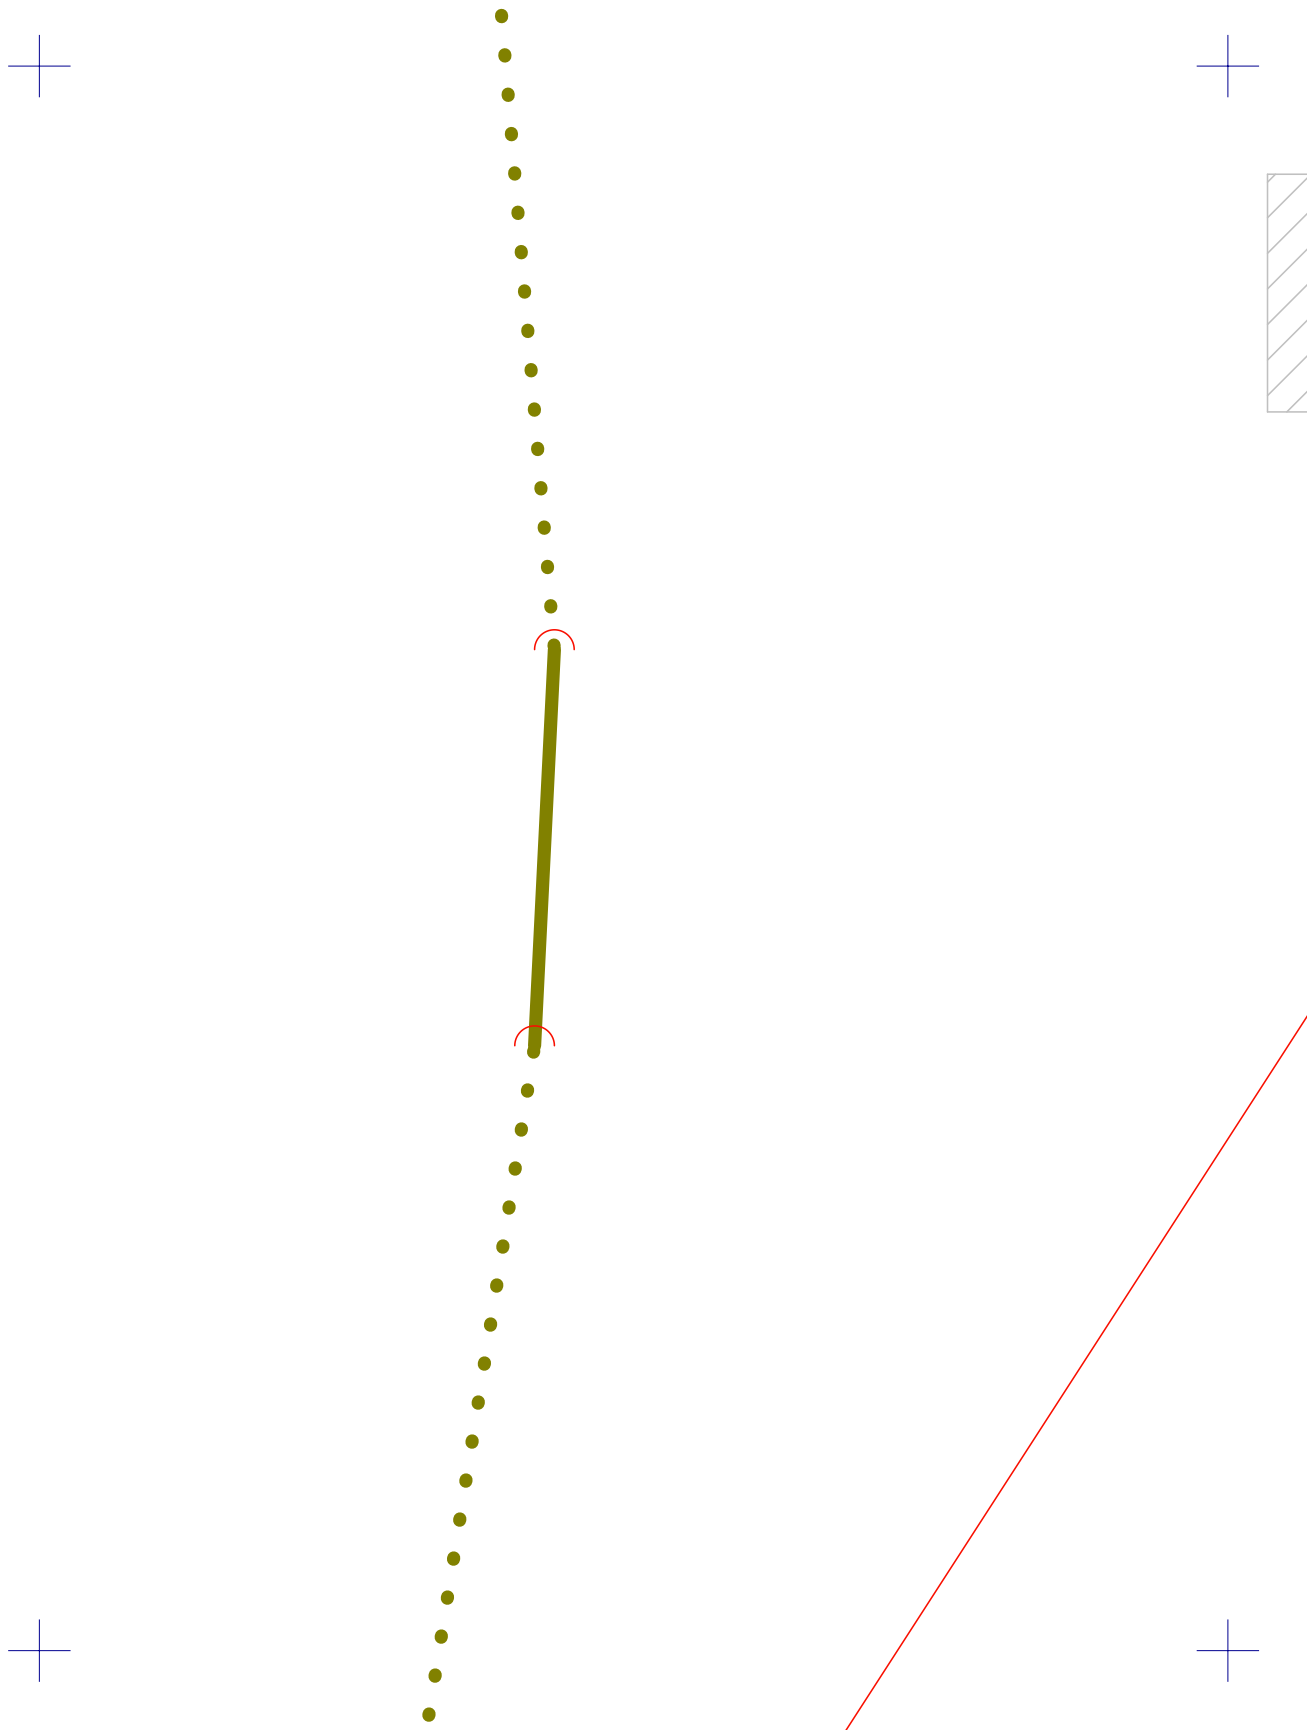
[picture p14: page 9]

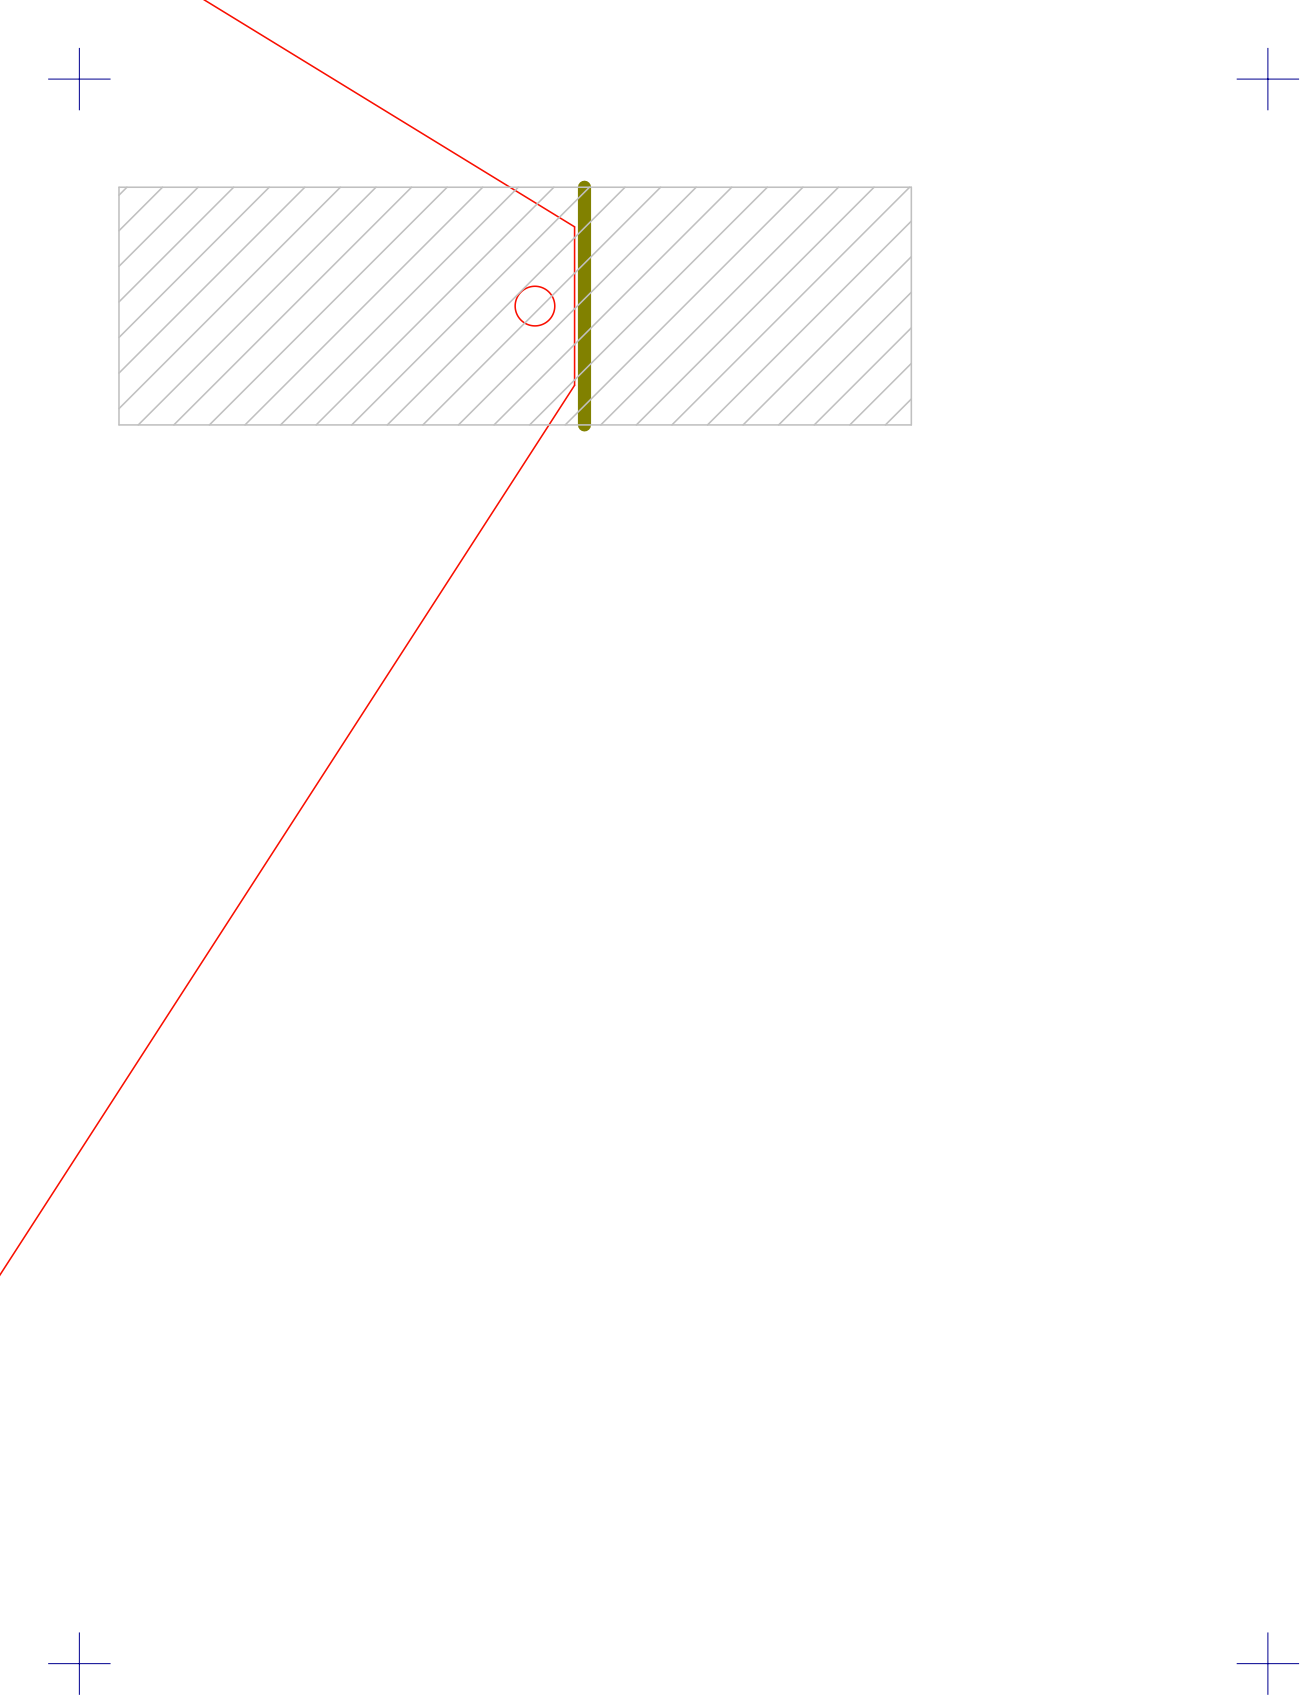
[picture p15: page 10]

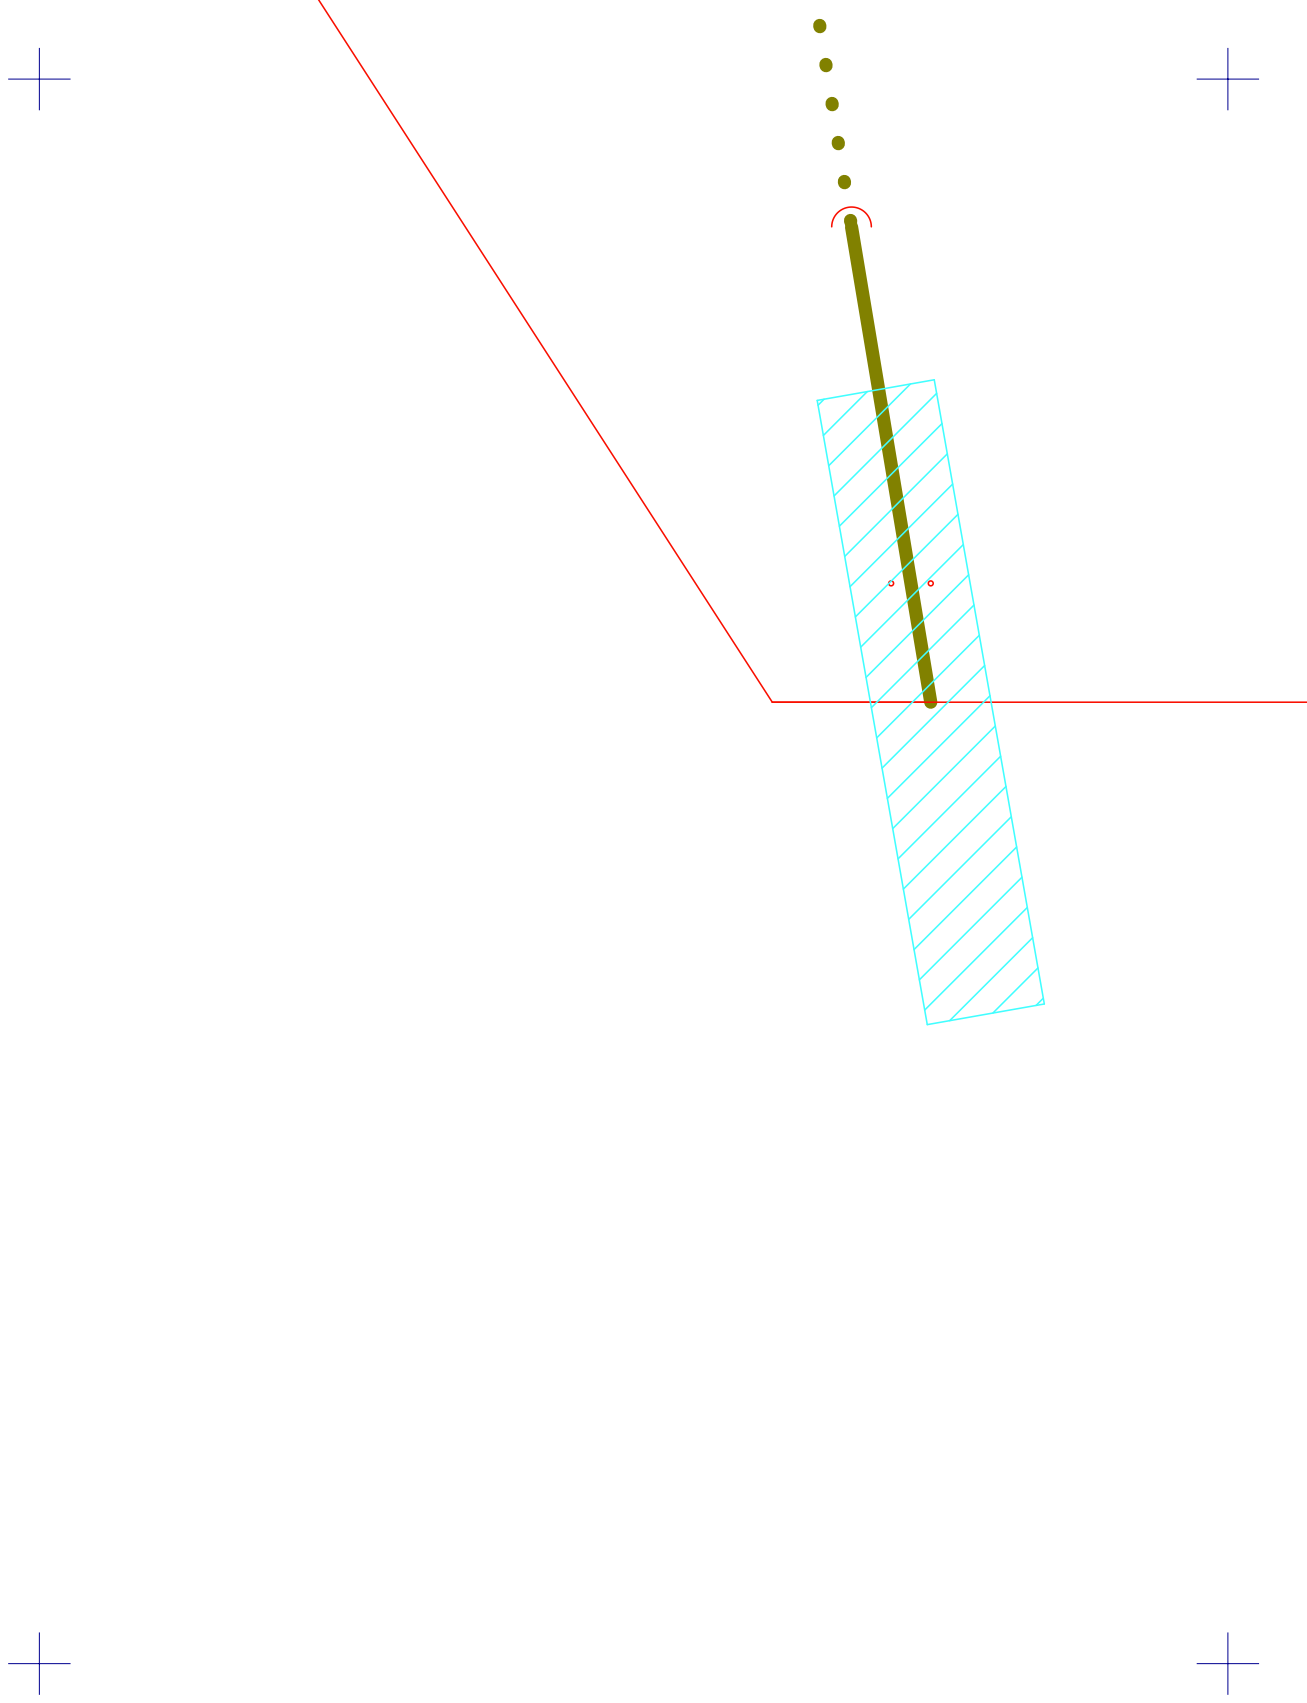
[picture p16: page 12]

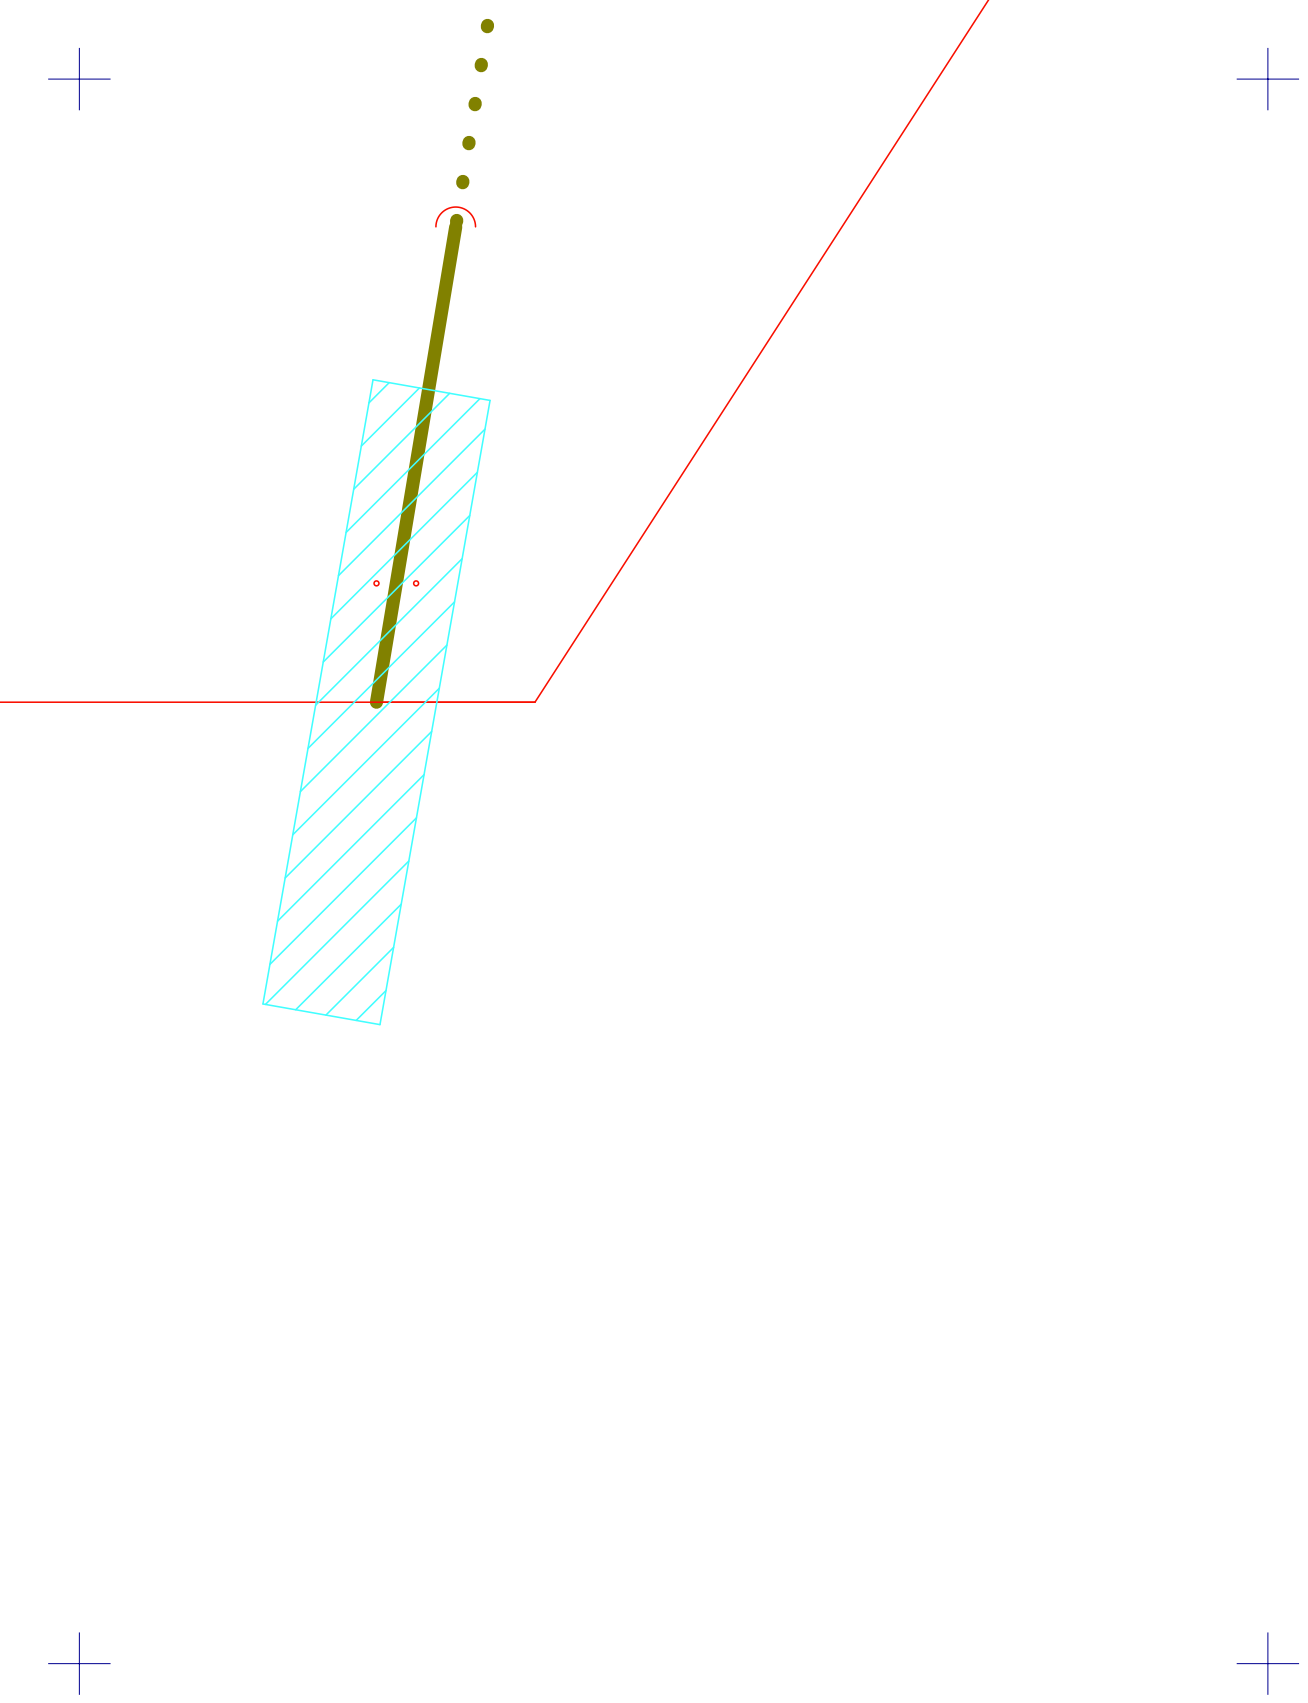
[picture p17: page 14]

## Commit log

2016-08-12 Removed TALA from repository-- decided it need its own for neatness
    [TALA.dxf]
2016-08-13 Repo structure update
    added a contribute.md file, substantially edited the Readme for content
    and interconnection to the Kite Wind Speed Meter repository
    [TALA.bak000.dxf, TALA.dxf]
2016-08-13 Updated Readme
    moved some text around, put “designers” section below the kit
    description.
2016-08-25 Fixed horizontal width of TALA & bridle
    fixed the horizontal width of the central rectangle of the kite’s main
    sheet (which was off of the original dimension) and made the
    half-bridles straight, so the end loop is no longer displayed.
    [TALA.dxf]
2016-08-26 new print files, notes from the manual
    added notes on kite calibration and maintenance to the TALA_Kite folder
    added print files for assembly
    added notes from the manual on correcting measurements to extrapolate
    air speed to TALA_Measurement
    [TALA.bak000.dxf, ~TALA.dxf]
2016-08-26 re-wrote contribute.md to follow Open open source principles
    and expanded contribution options beyond this specific repository. I
    re-named it contributing.md to follow the conventions of open open
    source, and modified links in the readme.md to be ./ internal project
    links rather than web links.
    [~TALA.dxf]
2016-10-31 Added side of the kite to tie the tail to CAD file
    [TALA.dxf]
2016-11-22 Updated assembly with materials and extended tail/bridle info
2017-03-16 corrections to assembly instructions
2017-03-17 Added bill of materials spreadsheet
    added bill of materials as well as prices and suppliers list for kite
    parts, assembly tools, flight & line handling, and measurement tools
    [TALA_BOM.ods]
2017-03-17 BOM updates
    [TALA_BOM.ods]
2018-09-24 dxf updates for clarity
    [TALA.dxf]
